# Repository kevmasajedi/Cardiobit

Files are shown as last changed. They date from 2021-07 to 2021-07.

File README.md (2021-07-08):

# CardioBit
## A Smart, Opensource and Affordable Electrocardiography Platform
CardioBit is an architecture for building IoT capable, precise, scalable and cost-efficient ECG Devices. IoT-capability and affordability are the central dogmas of this architecture. This is mainly achieved by using opensource hardware, minimum reliance on specialty components, offloading signal processing tasks to the server and avoiding the use of costly isolation components - yet ensuing safety by relying solely on battery power.

## Introduction
In the wake of COVID-19 pandemic, in many countries throughout the world, medical infrastructure is seriously overwhelmed by a novel coronavirus. The vast majority of medical equipment are heavily patented and are sold in small volumes. Further, there is evidence that some entities actively prevented medical treatments from being deployed, even in the current pandemic. This model obviously fails during critical times. On the other hand, deployment of opensource hardware and software platforms, can result in significant cost reduction as well as increased critical preparedness. (Pearce 2020)

The potential of opensource platforms to facilitate the formation of inclusive, potentially worldwide research communities, have also captured my imagination. Economically
viable solutions can be derived out of the core architecture discussed here, and can be manufactured and deployed throughout the world, in a distributed fashion. In additon, a 12-lead proof-of-concept hardware is provided.

## Background
Readers are assumed to have a minimal background in physiology and electrical engineering. Namely, they are assumed to be familiar with the basic morphological characteristics of electrocardiogram and their physiological significance, and familiarity with ohm’s law, impedance, basic circuit theory, RC analog filters and basic operational amplifier circuits. However, prospective readers are encouraged to continue, as proper reference for further consultation is given in due course. For introductory topics in cardiac physiology see (Guyton and Hall 2015), and for basic introduction to electrical engineering concepts regard (Scherz and Monk 2016) and (Mancini and Carter 2009)

The simplest model for relating the electrical activity of the heart to the body surface potentials, is the single dipole model. As an action potential propagates through the cell, in the interface of depolarizing and resting tissue, there’s an intracellular current flow in the same direction of the action potential propagation. There is also an equal extra cellular current flowing against the direction of propagation. Therefore, charge is conserved and all the current loops in the conductive media form a single field, called “dipole field” (Figure 1). (Gari, Francisco and Patrick 2006)

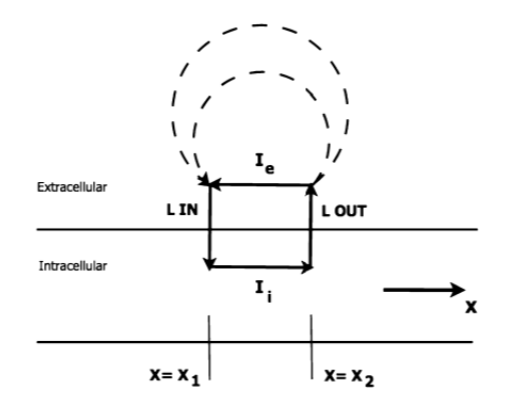
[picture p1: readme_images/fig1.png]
Figure 1. Flow of bioelectricity in current loops, presenting four segments: an outward traversal of the cell membrane, an extracellular segment, an inward traversal of the cell membrane and an intracellular segment.
 

For modeling purposes, all the individual current dipoles can be considered to originate at a single point in space, and the total electrical activity of the heart can be represented as a single dipole, whose magnitude and direction is the vector summation of all the individual dipoles. (Madeiro, et al. 2019)

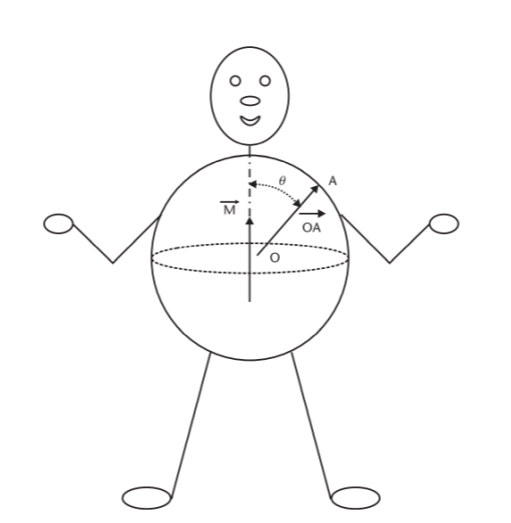
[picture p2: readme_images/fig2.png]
Figure 2. The Idealized spherical torso with the centrally located cardiac source


Let M(t) be the resultant vector which changes in the magnitude and direction as the function of time, potential distribution on the torso can be obtained by solving the Laplace’s equation as: (Gari, Francisco and Patrick 2006)

 

Where 𝜎 is the conductivity of the body electrolytic medium, |M(t)| is the magnitude of heart vector, θ(t) is the angle between the heart vector M(t) and the lead vector joining the center of the sphere to the point of surface potential measurement (Figure 2). Therefore, potential difference between two points in the torso can be given as: (Gari, Francisco and Patrick 2006)

 

Where 𝐿𝐴𝐵(𝑡) refers to the lead vector containing different points A and B of observation (e.g., electrodes) on the torso. For more elaborate discussion regarding the derivation of the abovementioned equations, please refer to (Mark 2004)

###  🎯 Design Decision I: Platform must be able to reconstruct 12 virtual leads from a reduced lead set
Equation 2.2 is important, as it states that the potential vector between two given electrodes (which essentially comprises the ECG signal in the respective lead) can be reconstructed if M(t) and the angle between M(t) and the lead vector 𝐿𝐴𝐵(𝑡) are known. As demonstrated later in the proof of concepts, the reconstruction of a virtual 12-Lead ECG from a reduced lead set is attempted in software, with satisfactory results.

However, it should be emphasized that equation 2.1 is derived with the implicit assumption of body as an idealized spherical torso, as shown in Figure 2. As a matter of fact, not only torso is far from an idealized sphere, but also it has non uniform conductance 𝜎 and its impedance can change during the cycle of respiration as well. (Gari, Francisco and Patrick 2006) So, for critical applications (e.g., in critically ill, unstable patients or in studying conditions that require exact monitoring) it is highly recommended to rely on standard 12-Lead ECG as opposed to the virtual case discussed above. 

In overall, this ability is helpful in that it provides the clinicians in unprivileged areas with more data without additional costs. Thus, it helps in cases which wide availability of ECG monitoring is the primary goal. For example, when secondary prevention (i.e., screening) of ischemic or heart rhythm disease is to be performed on a disperse population in a large geographic area.

***

## Signal Acquisition:
### Electrode-Patient Interface:
The electrical activity of the heart is propagated throughout the body by ions. To measure this activity at body surface, conversion of ions to electrons, is needed. This conversion happens at electrode-patient interface. When a metallic electrode (most commonly silver-silver chloride) is in contact with an electrolyte (skin or electrode gel), an electrochemical reaction occurs by ionexchange. Metal atoms (𝑀) tend to lose n electrons and pass into the electrolyte as metal ions (𝑀+𝑛 ) causing the electrode to become negatively charged with respect to the electrolyte: (Webster 2006)

 

Similarly, under equilibrium, ions in the electrolyte take the reverse direction of the equation (3.1). The electrode becomes positively charged with respect to the electrolyte as a result. (Webster 2006)

 

Under equilibrium condition, rate at which metal atoms lose electrons and pass into the electrolyte is exactly balanced by the rate of equation (3.2). Thus, the current flowing in one direction, cancels out the current flowing in the opposing direction, resulting in zero net current flow. However, a potential difference is found to exist between the electrode and electrolyte and depends on the position of the equilibrium between two processes (3.1) and (3.2). This potential is termed as half-cell potential, and can be calculated by the Nernst Equation (3.3) (Webster 2006)

𝐸0 is the standard half-cell potential measured relative to the standard hydrogen electrode, R is the universal gas constant, n is the number of electrons involved in the reaction, T is the absolute temperature in Kelvin. F is the faraday’s constant.

Since an ECG signal is obtained by two equal electrodes for each lead, it can be assumed that half-cell potentials are equal and offset voltage at the input of differential amplifier is zero. In practice, small differences in the properties of electrodes result in a dc offset voltage, which can sometimes change over time. (Madeiro, et al. 2019)

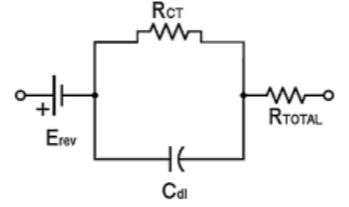
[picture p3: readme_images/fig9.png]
Figure 3. Electrode-Patient Interface Equivalent Circuit. 𝐶𝑑𝑙 the double-layer capacitance; 𝑅𝐶𝑇 the charge transfer resistance; 𝑅𝑇𝑂𝑇𝐴𝐿 lead and electrode resistances and 𝐸𝑅𝐸𝑉 the equilibrium (Nernst) potential.


Further, as positive ions are attracted by the electrode and negative ions by the electrolyte, a double layer capacitance is created at the electrode-patient interface. Also, due to the electrochemical reactions in the interface, some dc current can leak across the double layer. The amount of leak is proportional to charge transfer resistance which is calculated by the equation (3.4) where 𝑖0 is the current flowing across the interface in both directions (no flow under equilibrium, as discussed before). The equivalent circuit is shown in Figure 3. (Madeiro, et al. 2019) Note that equations (3.3) and (3.4) are only of theoretical interest here.

 

###  🎯 Design Decision II: Cost-optimized solutions should be supplied with higher voltage
DC offset voltage discussed above, can be as high as 300mV which is enormous when compared to typical 1.8mV amplitude of the ECG signal (Lee and Kruse 2008). The dc offset can be reduced by the use of high-quality electrodes or significantly suppressed with specialty circuits (Huang, Huang and Li 2018). However, in accordance with the design principles discussed in the abstract of this article, a simple rule of thumb is proposed instead: Use higher supply voltage, when designing cost-optimized solutions.

To put this design decision in better context, we need to slightly deviate from the flow of the discussion:

>As ECG signal is very weak with only 0.5µV – 4mV of amplitude and is susceptible to interference [e.g., 50 or 60Hz AC noise which is present in virtually all indoor environments], it needs to be amplified before processing and analysis. (Huang, Huang and Li 2018)

>A high dc offset voltage can quickly saturate a low-voltage circuit and limit the amount of achievable amplification. For example, a 3V supply voltage (equivalent to -1.5v to +1.5v dual supply), can be easily saturated by only a 5 times front-end amplification. Thus, only 2x to 3x first-stage gain can be reasonably applied. A high-resolution signal can still be obtained after a second-stage amplification and by the use of a high-precision analog-todigital converter (ADC). But as discussed later, due to low front-end amplification the noise profile will not be satisfactory. In addition, high-precision ADCs can be costly and usually have far slower sampling rates.

Thus, for designing cost-optimized solution, a supply voltage of at least 12V (-6.0v to +6.0v) is recommended. As CardioBit is designed for battery-powered operation, and high-capacity 3.7v 18650 Lithium-Ion cells are widely available with ever decreasing cost (Warner 2015), such supply voltage can be provided with 3 to 4 cells in series, allowing for a compact form-factor for the final, assembled device.

***

### Surface Lead Systems:
The standard 12-Lead ECG is a noninvasive representation of the electrical activity of the heart. This lead system rests on the theoretical foundation of classical lead theory introduced by Einthoven et al. (Madeiro, et al. 2019) This theory assumes a single time-varying dipole in 2- dimensional space to represent electrical activity of the heart, and assumes human body as a homogenous conductor. Later, Burger and van Millan improved and generalized the theory (Burger and van Milaan 1948) with regard to 3-dimentionality and non-homogenous conductance of the body. Yet, their theory still rests on the fixed-dipole hypothesis, thus allows for the derivation of the potentials at a given instance, anywhere on the body surface (Macfarlane, et al. 2011). As noted in [Design Decision I](https://github.com/kevmasajedi/Cardiobit/blob/main/README.md#-design-decision-i-platform-must-be-able-to-reconstruct-12-virtual-leads-from-a-reduced-lead-set), these assumptions are not completely solid.

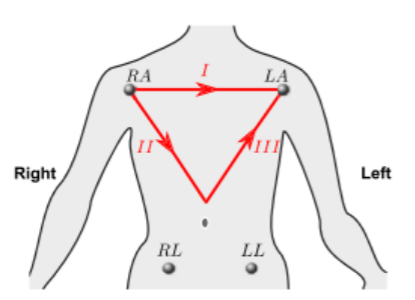
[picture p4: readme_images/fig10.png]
Figure 4. Bipolar Limb Leads.


12 Leads on this system are composed of 3 bipolar limb leads(I, II, III), 3 augmented unipolar limb leads (aVR, aVL and aVF) and 6 unipolar chest leads (𝑉1 𝑡𝑜 𝑉6). Bipolar limb leads are defined by equations 3.5, 3.6, 3.7. (Figure 4). Right leg electrode is used for reducing electromagnetic interference, and can be placed anywhere at body surface. It is placed at right leg for convenience. (Madeiro, et al. 2019).

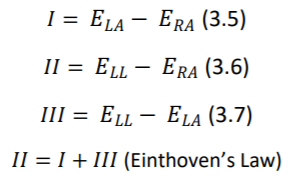
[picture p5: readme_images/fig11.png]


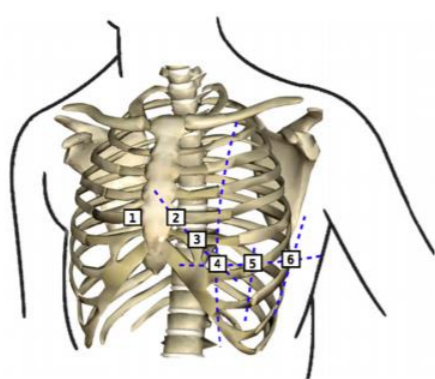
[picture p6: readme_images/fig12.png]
Figure 5. Position of unipolar chest leads


Potentials of unipolar chest electrodes (𝑉1 𝑡𝑜 𝑉6) is measured relative to Wilson Central Terminal (WCT), which is the normalized sum of the potentials of 𝐸𝐿𝐴, 𝐸𝑅𝐴 and 𝐸𝐿𝐿. (Equations 3.8 and 3.9) (Madeiro, et al. 2019)



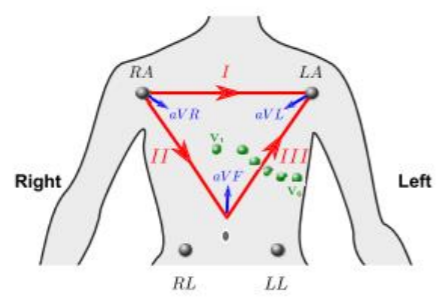
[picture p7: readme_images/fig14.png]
Figure 6. Standard 12-Lead System


Augmented unipolar limb leads, comprise the remaining three leads. The same set of electrodes from bipolar leads are used (𝐸𝐿𝐴, 𝐸𝑅𝐴 and 𝐸𝐿𝐿) as positive electrodes and negative electrode is a modified version of the Wilson Central Terminal called of GT. (equations 3.10 through 3.12) (Madeiro, et al. 2019)

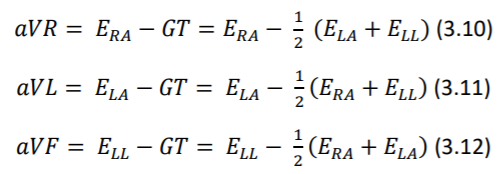
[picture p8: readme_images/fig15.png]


###  🎯 Design Decision III: Technical issues should be openly discussed, anyone’s contribution is to be welcomed
A variety of other lead systems are proposed, including Frank, reduced Frank, EASI or various three or two lead configurations. (Gari, Francisco and Patrick 2006). But the standard 12-Lead system has by far the widest adoption in clinical practice. Thus, other configurations are not discussed further. 

However, CardioBit is opensource in hardware and software and it can be adopted for any given lead set, by any interested researcher. In fact, as the author, I’ll be delighted If I see such actions taken by the potential research and development community. I believe community, can shed more light on the issue of practicality of virtual 12-Lead ECG reconstruction from a reduced lead set, provide a quantitative measure of accuracy for such reconstructions, or even come up with a more theoretically solid method of reconstruction (e.g., based on the modern concept of leadfield instead of lead-vector)

In that spirit, I like to echo a section of *ST Segment Monitoring Practice Guideline Working Group*’s recommendation regarding the use of reduced lead sets, which is further discussed by (Gari, Francisco and Patrick 2006):

- If only two leads are available for ST segment monitoring (for patients with acute coronary syndrome), lead III and V3 should be used.
- The best three-lead combination is III-V3-V5
- V1, is considered the best lead to monitor for cardiac arrhythmias
- The use of at least three chest leads (V3, V4, V5) is recommended for ST analysis

The provided proof-of-concept of the CardioBit platform’s core architecture, is designed for acquisition of 2 bipolar limb leads and 2 unipolar chest leads. User (whether clinician, researcher or developer) can decide which respective two leads he or she wants to use. As noted, reconstruction of virtual 12-lead ECG from the chosen leads is attempted in software. It is left up to user to decide whether to use this feature or not. For more information, please regard the factors noted in  [Design Decision I](https://github.com/kevmasajedi/Cardiobit/blob/main/README.md#-design-decision-i-platform-must-be-able-to-reconstruct-12-virtual-leads-from-a-reduced-lead-set)
***
## Electrical Design
### The Characteristics of Measured Biopotential

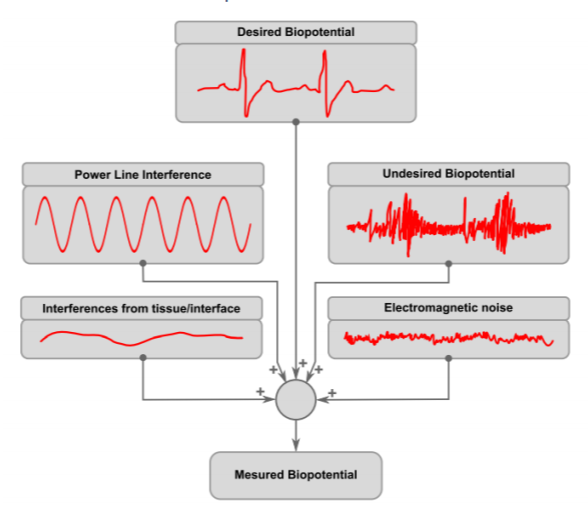
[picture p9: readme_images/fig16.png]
Figure 7. Components of measured biopotential. (Credit: Madeiro, et al. 2019)


As stated before, surface potentials representing ECG signal are very weak (a few millivolts maximum) and are riding on a comparatively enormous offset voltage (hundreds of millivolts). (Lee and Kruse 2008) To complicate matters further, these signals are often contaminated with biopotential activity of muscles and nerves beneath the electrodes, 50Hz/60Hz AC powerline interference, low frequency motion artifacts and all sorts of high frequency electromagnetic noise (Madeiro, et al. 2019)

Among these parasitic sources, the AC interference may be the most troublesome. Low frequency motion artifacts can be dealt with by good skin preparation and good electrode adhesion. Also, biopotential artifacts of nerve and muscle activity will be negligible if patient remain still and relaxed at a comfortable position. Lastly, high frequency noise, can be easily suppressed by a simple analog RC filter and later by digital filtering. Conversely, AC interference is present virtually anywhere and its frequency falls in the normal frequency range of ECG signal (0.05Hz – 250Hz)

Unfortunately, AC interference is unavoidably present in any clinical situation. This interference can be of two independent types: magnetic and electric: A changing magnetic field produced by AC powerlines can induce in any nearby conductive loop, an electromotive force, which results in an ac potential. A changing electric field can also produce interference by causing ac currents to flow to ground through the system. (Huhta and Webster 1973)

The magnetic interference is directly proportional to the area of the loop formed between two electrode leads and reducing this area is the best way to reduce this type of interference. Expensive shielding of the wires does not prevent this kind of interference. (As shown in Figure 8.) (Huhta and Webster 1973)

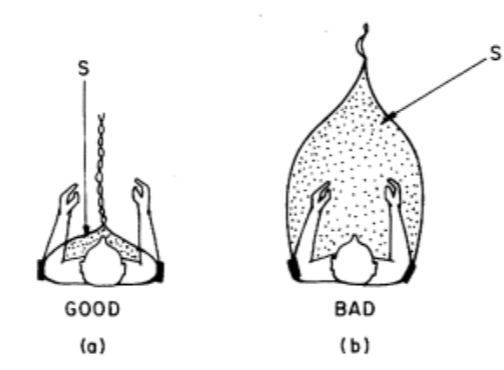
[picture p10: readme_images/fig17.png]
Figure 8. AC noise pickup by magnetic interference. (Credit: Huhta and Webster 1973)


The electrical interference is modeled as the capacitive coupling of AC powerlines to lead wirings, which results in displacement current induced in the respective leads, because the length of the leads is almost the same and the wires run closely together, this displacement current should be approximately equal in each lead. (Huhta and Webster 1973)

Assuming that electrodes have perfectly the same electrical impedance, such displacement current should be rejected. Because, the front-end differential amplifier, only amplifies the difference between the voltages of the two inputs. In other words, as impedance of both electrodes is the same, the displacement current, results in induction of exactly the same voltage in them. This can be easily stated using generalized ohm’s law (Equation 3.13).



Where 𝑉_𝐴𝐶 is the AC interference potential, 𝐼_𝐷 is the displacement current and Z is the impedance in respective inputs A and B. It is observed that 𝑉_𝐴𝐶 is induced by unbalance of the two impedances (the term 𝑍_𝐴 − 𝑍_𝐵 being non-zero). (Huhta and Webster 1973)

That being said, it should not come as a surprise, that no two electrodes are perfectly the same in real world. Electrode impedance at 60Hz may range from less than 1 KΩ up to 100 KΩ. Given typical values of 6 nA of 𝐼𝐷 in a 3-m length of unshielded wire, and typical impedance imbalance of 5KΩ, induced potential (𝑉𝐴𝐶) would be about 30µV which is roughly 3 percent of the ECG potential. (Huhta and Webster 1973)

Author should note here that in the experimentation with lower quality, cheaper disposable electrodes, far higher impedance imbalance has been observed and induced potential frequency observed to be as much as 10% of the QRS potential. Such observations influenced the [Design Decision IV](https://github.com/kevmasajedi/Cardiobit/blob/main/README.md#-design-decision-iv-use-heavy-dsp-instead-of-fancy-analog-circuits) which will be discussed in due course.

### Analog Front End Circuit
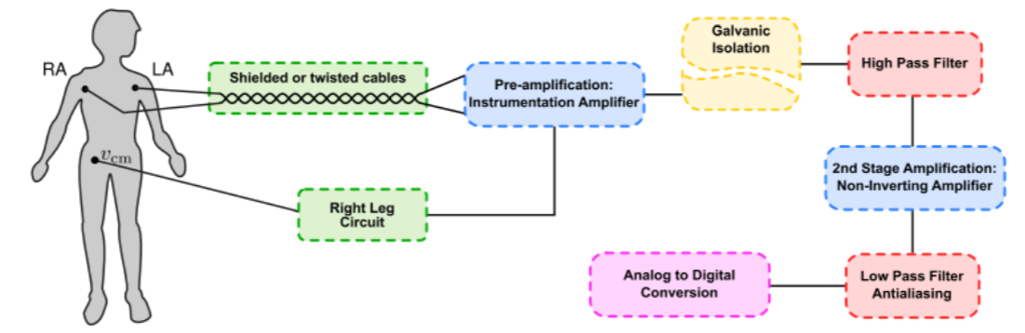
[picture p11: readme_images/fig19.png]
Figure 9. A classical topology of ECG analog front end topology. (Credit: Madeiro, et al. 2019)

Figure 9, shows a classical topology of ECG analog front end signal conditioner. Here, the intention of each stage in this block diagram is briefly discussed:

#### Shielded or Twisted Cables:
- Twisted cables minimize the area occupied by the loop forming between electrode leads and the body, thereby reduce the magnetic interference of AC powerlines. As discussed in the section 3.3.1 and shown in Figure 8. Shielding provides a measure against electrical interference of AC powerlines, by providing a grounded surface near the lead wires, thereby significantly reduces capacitive coupling of powerlines with lead wires. Consult (Huhta and Webster 1973) for more detailed discussion.

#### Pre-Amplification by Instrumentation Amplifier:

- Instrumentation Amplifiers are modified types of operational amplifiers. They are differential amplifiers with a very high (theoretically infinite) input impedance and improved CMRR. This large input impedance, is essential to ensure no current is being drawn from the body, and thus the small voltage of ECG signal is properly measured. In short, the chain of reasoning for this, is very similar to that of well-known ideal voltmeter, which should have infinite resistance and no current should flow through it. See (Horowitz and Hill 2015) or (Scherz and Monk 2016).
- Common-Mode Rejection Ratio (CMRR) indicates the ratio between the differential gain of an amplifier (𝐺𝐷) and its common-mode gain (𝐺𝐶). (Equation 3.14) Common mode signals are those that appear simultaneously on both inputs (e.g., that of 60/50-Hz powerline interference). Ideally, CMRR of a differential amplifier should be infinite. However, that’s not achievable in practice. Instrumentation amplifiers enjoy a higher CMRR than those of ordinary operational amplifiers, due to their special configuration. The value of CMRR changes with gain and frequency, and typically ranges between 80dB to 120dB. See (Horowitz and Hill 2015).
- Last to be noted under this topic, is the necessity of pre-amplification per se. As discussed before, the desired ECG signal is very weak and is floating on a large-by-comparison voltage offset, created by unequal Nernst potential in respective electrodes. This limits the amount of gain applicable to the first stage amplification. In addition, low frequency noise resulting from poor skin preparation or poor electrode adhesion can further complicate the problem. Thus, a large first-stage gain would result in quick saturation and/or large wandering of output signal of the circuit. Dividing amplification in two stages, can significantly alleviate these problems and yet adequately amplify the signal to meet the dynamic range of analog-to-digital converter. (Madeiro, et al. 2019)
- Author proposes a coarse rule of thumb for determining first-stage gain: divide supply voltage by 0.3 and do not exceed one-fourth of the result. For example, a supply voltage of 12v (+6v to -6v) should have maximum first stage gain of ( 12/0.3 × 1/4 = 10). The divisor 0.3 comes from taking into account a typically high electrode offset voltage of ∓ 300mV. It is divided by four to ensure amplified offset does not saturate more than half of negative or positive voltage rails.

#### Right Leg Drive Circuit:
- This circuit inverts and amplifies the common-mode voltage and feeds it back to the body. As a result, it can help to reduce noises that are induced on both of the electrode leads (e.g., AC powerline noise). (Madeiro, et al. 2019) Unfortunately, this circuit can easily become unstable, and thus not implemented in CardioBit proof-of- concept hardware (more on the reason in [Design Decision IV](https://github.com/kevmasajedi/Cardiobit/blob/main/README.md#-design-decision-iv-use-heavy-dsp-instead-of-fancy-analog-circuits)). This circuit is extensively discussed in literature and interested readers are referred to (Webster 2006)

#### Galvanic Isolation:
- Safety precautions should be taken seriously when a circuit that is connected to the mains electricity, comes into contact with human subject. Even very small current leakages (less than 100µA) can induce lethal ventricular fibrillation in catheterized human subjects. 
- In such circumstances, circuit board must be segmented into isolated and non-isolated sections. These sections must be separated by at least 10mm of free space from each other (depending on the dielectric constant of the PCB) Isolated sections should receive power from non-isolated section via DC-to-DC converters. Similarly, information (ECG signal) is transmitted back to the non-isolated parts through opto-isolators or isolation amplifiers. (Gari, Francisco and Patrick 2006)
- ⚠ As discussed in the [Design Decision V](https://github.com/kevmasajedi/Cardiobit/blob/main/README.md#-design-decision-v-design-for-battery-powered-operation-only), and in accordance with the design principles discussed in the abstract, **CardioBit, is designed ONLY for low-voltage DC battery-powered usage.** The proof-of-concept circuit is not isolated and should not be directly (via AC-to-DC adapter) or indirectly (via USB port to a mains-powered PC or even a laptop that is connected via an adapter to AC power) connected to the wall outlets, unless it is completely disconnected from human subject. The operator, is responsible for any shortcomings in protecting patient safety, when he or she ignores these precautions.
- As CardioBit is opensource, any community developed hardware is advised to come with precise documentation clearly describing the specific solution’s do’s and don’ts regarding patient safety.

#### High-Pass Filter:
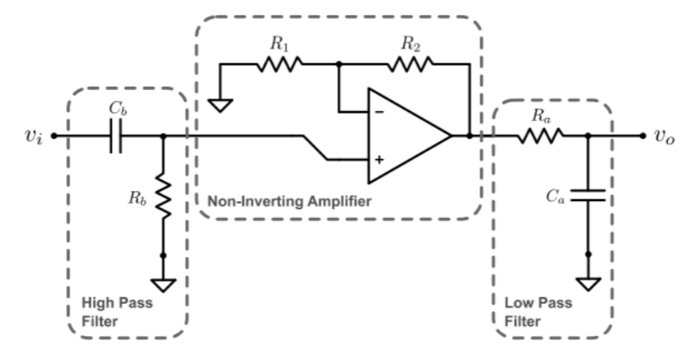
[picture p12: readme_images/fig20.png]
Figure 10. Depicting HPF, Second-Stage Amplification and LPF stages


- As previously discussed, half-cell potential differences at electrodes result in a DC offset which gets amplified in the first stage and can possibly saturate the voltage rails if high amplification is applied. In addition, changes in skin moisture, temperature, muscle tremor, movement, electrode gel leakage and patient’s breathing, result in slowly varying electrode impedance which manifests itself as a slow wandering of the ECG baseline. (Madeiro, et al. 2019) A simple RC filter can ground the signals below a cutoff frequency 𝑓𝑐 , which is determined by choosing the values of the resistor R and the capacitor C. (Equation 3.14) However as discussed in (G), using an active filter might be a better option.



#### Second Stage Amplification:
- As high-pass filter, removes the effect of offset voltage, higher amplification can be achieved in the second stage. The amount of the amplification should be determined by both considering supply voltage of the circuit and dynamic range of the analog-to-digital converter. One must ensure a high-voltage QRS complex would not saturate the voltage rails. Minimum amplification for a desirable dynamic range can be determined by looking for the u-waves in the acquired signal. If these waves are readily recorded, it can be reasonably assumed that amplification is sufficient for analog-digital converter to faithfully record the signal.

#### Second Stage Amplification:
- As high-pass filter, removes the effect of offset voltage, higher amplification can be achieved in the second stage. The amount of the amplification should be determined by both considering supply voltage of the circuit and dynamic range of the analog-to-digital converter. One must ensure a high-voltage QRS complex would not saturate the voltage rails. Minimum amplification for a desirable dynamic range can be determined by looking for the u-waves in the acquired signal. If these waves are readily recorded, it can be reasonably assumed that amplification is sufficient for analog-digital converter to faithfully record the signal.

#### Low Pass Filter:
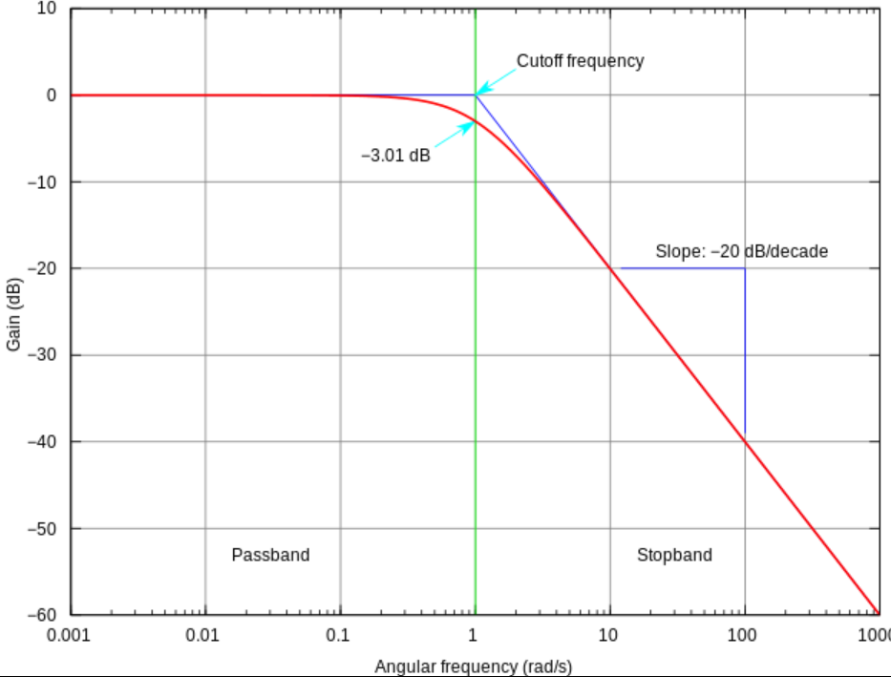
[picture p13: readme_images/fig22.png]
Figure 11. Frequency response of RC filters. Roll-off of simple RC low pass filters, is only about -20 dB/decade (credit: wikipedia)


- high frequency electromagnetic interference, and skeletal muscle activity, can also contaminate the recorded biopotential, especially during exercise or under 24/7 continuous (Holter) monitoring. These high frequency components should be filtered, in a way that does not cause distortion on ECG signal (e.g., blunting of the QRS peak). Attempting to rely solely on the slow sampling frequency of analog-to-digital converter (ADC), to filter such components, will result in a signal corrupted by aliasing effect. Refer to (Parker 2017) for an introduction.
- In order to avoid aliasing, Nyquist theorem dictates the cutoff frequency of the low pass filter (equation 3.14) should be less than half the sampling frequency of ADC. Kligfield, et al. suggested 0.05 Hz to 250 Hz to be the frequency band of desired ECG signal. If adult patients are under monitoring, the cutoff of the lowpass filter can be reduced to 150 Hz. So, the ADC must feature a sampling frequency of at least 301 Hz.
- A simple low-pass filter is used in the proof-of-concept of the core architecture. But theoretically, this may not be a good choice. First, simple RC filters suffer from a poor rolloff of about -20 dB/decade. Meaning signals with 10 times the frequency of filter’s cutoff will still be present with one-tenth of original voltage. So, noises which have frequencies close to the cut-off, will remain significant and may still cause prominent aliasing to occur.
- High-order active filters can instead be used with more ideal performance, but designer needs to beware occasional ringing behavior near cut-off frequency. High-order Bessel filters are recommended for their linear response and minimal distortion (Madeiro, et al. 2019). I avoid discussing details here, as they are far from the scope of this article. However, in [Design Decision IV](https://github.com/kevmasajedi/Cardiobit/blob/main/README.md#-design-decision-iv-use-heavy-dsp-instead-of-fancy-analog-circuits), I discuss why simple RC filters are used in core architecture’s proof-of-concept.

#### Analog to Digital Conversion:
- Lastly, the acquired biopotential will be converted to digital representation by a delta-sigma analog-to-digital converter, with a sampling frequency of at least twice the cut-off frequency of the low-pass filter. The digital signal will be further processed with embedded microcontroller (Based on Arduino or ESP8266 platforms) as discussed later.

### 🎯 Design Decision IV: Use Heavy DSP Instead of Fancy Analog Circuits
This design decision, has been referred to, as early as Section 3.3.1, in relation to the issue of impedance imbalance of low-quality electrodes, and later, in 3.3.2 (C), in relation to right-leg circuit, and then, in 3.3.2 (G) in relation to RC filters. However, actual presentation of this designdecision has been delayed until now, because sufficient background should have been discussed for it in order to make sense. 

The design decision IV is about the approach to noise-suppression. As we learned, ECG signal is inevitably contaminated by noise. The issue is how to filter out and suppress the noise, without distorting the signal. Additionally, the core-architecture should be open-source, inclusive and cost-optimized. So, the solution, should not be overly elaborate, as it discourages contribution. Less-privileged users should also be kept in mind, so worst-case scenarios of poor-quality electrodes with large offset voltage and high impedance imbalance should be assumed throughout the design.

As a result, author decided against the use of right-leg drive circuit, as it is unstable by design and requires fine-tuning or fancy design techniques to work properly, which reduces scalability and inclusivity of platform. 

In the same spirit, simple first-order RC filters have been preferred over more complicated eighth-order active Bessel filters. However, in this case, the compromise sometimes manifests itself. Unfortunately, designer is sometimes forced to reduce cut-off frequency of the low pass filter below 150 Hz, to prevent aliasing in cases where sampling frequency of ADC is close to 300- Hz (which is not a rare issue in low-cost ADCs). Also, the R wave in the QRS complex may become mildly blunt, which may be tolerable in some applications, but not in some others. 

Such analog minimalism, will be later met with aggressive digital signal processing, on the server side, which can be flexibly tuned by the user through a web-based user interface. For example, User may enable, disable or set filtering frequency, etc. Please refer to (Parker 2017) for theoretical introduction on the subject. For enquiry about the detailed implementation of these features, please refer to the proof-of-concept hardware documentations. 

In overall, this decision may render the bare-bone, core-architecture unsuitable for some critical research or clinical applications. But then again, that’s not the intended use-case. The core architecture is designed as a starting platform for other solutions to be built upon it. I believe, overtime, a vibrant community can more than compensate such technical shortcomings. So, one must design the core platform as generic as possible, rather than prohibitively opinionated and elaborate. Later, more complete products can be made based on the core platform.

### 🎯 Design Decision V: Design for Battery-Powered Operation Only
CardioBit is also designed with a look toward distributed manufacturing. The casing, provided for the proof-of-concept hardware, can be readily made with a 3D printer, the PCB can be prototyped for just a few dollars and can be assembled in any electronicslaboratory with minimal equipment. Anyone, anywhere in the world can tweak the proof-of-concept hardware, or improve the design to make it more suitable for specific applications. 

With this great customizability, comes great concernsfor patient safety. As previously stated, less than 100µA of 60-Hz AC leakage current, can result in lethal consequences in catheterized patients. Although measures can be taken to ensure such leaks will not happen (e.g., by electrical isolation of the analog front-end and the use of isolation amplifiers), and healthy, nonhospitalized individuals, may have higher thresholds and less vulnerability, one cannot simply hope that all the design guidelines will be properly implemented in community-designed solutions. In this regard, the risk is simply too great even for minor mistakes. 

Thus, it was decided against the use of AC power, altogether. The core architecture along with its proof-of-concepts are designed ONLY for battery-powered operation. They should not be connected to mains powerlines, either via the charging adapter, or via USB port to an AC powered PC or even a charging laptop. Developers who want to use the USB port to test their prototypes, are advised to use an isolated USB hub to minimize dangers. 

I believe this design decision, not only results in far better patient safety, it also honors the design principles, as the total cost of both components and development will be driven significantly lower. This way, the platform will be far more forgiving in case of design/assembly errors and so it will remain inviting to young, less experienced minds. 

Additionally, in the long run, lithium batteries will become even more affordable, developed products will become more energy-efficient, and more portable, and can be used in remote locations and unprivileged off-grid areas.

## Digital Circuitry:
CardioBit platform, does not use custom digital circuits, and it is designed to be compatible with open-source electronics platforms like Arduino. Arduino is an open-source, easy to use hardware and software platform. The Arduino-based boards are readily available virtually everywhere in the world in multiple form-factors with affordable prices. 

Originally, Arduino is based on 8-bit AVR microcontrollers. But as hardware is opensource, versions based on ESP8266 32-bit processor are also developed based on Arduino platform. This chip is more powerful, and features more memory, along with full TCP/IP stack for Wi-Fi connectivity. Many open-source libraries are developed for this chip to be programmed with Arduino software, using Arduino integrated development environment (IDE) and Arduino programming language.

CardioBit is not opinionated about which platform, or microcontroller is used for further processing. One can use Arduino, Raspberry Pi, Orange Pi, CircuitPython or essentially any open or closed-source platform to pair with the analog front-end. Only requirements are to power the ADCs used in the circuit with native voltage of the platform (3.3v or 5v), choose the value of endstage resistors to divide the voltage to the suitable value, and connect to ADCs with a communication interface (e.g., SPI or I2C). Connectivity to internet should also be provided, either natively or by using Wi-Fi or Ethernet shields, as digital signal processing is offloaded to server-side.

However, to be on par with our design principles, we based the proof-of-concept models for the core-architecture on ESP8266 powered hardware and Arduino platform software. Low-cost, lowpower, readily available ADS1015 ADC chips are used and accessed via I2C. These can be directly swapped with ADS1115 chips for low lead-count solutions, as this has higher accuracy but lower sampling rate which renders it too slow for 12-Lead devices.

## ⚠ Safety and Precautions
As already stated, multiple times, CardioBit core architecture and its proof-of-concept implementations are designed **ONLY** for battery-powered operation. Operator is solely responsible for patient safety if he or she uses the device while it’s plugged into AC power adapter or non-isolated computer USB port. (Please refer to [Design Decision V](https://github.com/kevmasajedi/Cardiobit/blob/main/README.md#-design-decision-v-design-for-battery-powered-operation-only))

Also, the core architecture and its proof-of-concept implementations, are not equipped with voltage-limiting input circuitry, and should not be relied upon in mission-critical applications, especially when defibrillators or other electrosurgical equipment are to be used. In such cases, high-voltage induced between two leads by such equipment, can damage the internal circuits and render the device non-working.

## References
- Burger, H.C., and J.B. van Milaan. 1948. "Heart-vector and leads, Part I." British Heart Journal
- Einthoven, W, G Fahr, and A DE Waart. 1950. "On the direction and manifest size of the variations of potential in the human heart and on the influence of the position of the heart on the form of the electrocardiogram." American Heart Journal
- Gari, D.C., A. Francisco, and E Patrick. 2006. Advanced Methods and Tools for ECG Data Analysis. Artech House, Inc.
- Guyton, Arthur C., and John E. Hall. 2015. Guyton and Hall Textbook of Medical Physiology. Saunders.
- Horowitz, Paul, and Winfield Hill. 2015. The Art of Electronics 3rd Edition. Cambridge University Press.
- Huang, Ji-Wei, Tai-Ming Huang, and Fan-Yang Li. 2018. "Design of a low electrode offset and high CMRR instrumentation." IEEE.
- Huhta, James C, and John G Webster. 1973. "60-Hz Interference in Electrocardiography." IEEE Transactions on biomedical engineering.
- Kligfield, P., L.S. Gettes, J.J. Bailey, R. Childers, B.J. Deal, E.W. Hancock, G. van Herpen, and Kors. 2007. "Recommendations for the Standardization and Interpretation of the Electrocardiogram." Circulation.
- Lee, Stephen, and John Kruse. 2008. "Biopotential Electrode Sensors in ECG/EEG/EMG Systems." Analog Devices.
- Macfarlane, Peter W., Adrian Van Ooosterom, Olle Pahlm, Paul Kligfield, and Michiel Janse. 2011. Comprehensive Electrocardiology, Second Edition. Springer.
- Madeiro, Joao Paulo do Vale, Paulo Cortez, José Maria Da Silva Monteiro Filho, and Angelo Roncalli Alencar Brayner. 2019. Developments and Applications for ECG Signal Processing. Academic Press.
- Mancini, Ron, and Bruce Carter. 2009. Op Amps for Everyone. Newnes.
- Mark, Roger. 2004. Quantitative Physiology: Organ Transport Systems, Lecture notes from HST/MIT Open Courseware .
- Parker, Michael. 2017. Digital Signal Processing 101. Newnes.
- Pearce, Joshua M. 2020. "A review of open source ventilators for COVID-19 and future pandemics [version 2; peer review: 3 approved]." F1000Research 3,4
- Scherz, Paul, and Simon Monk. 2016. Practical Electronics for Inventors. McGraw-Hill Education.
- Warner, John. 2015. The Handbook of Lithium-Ion Battery Pack Design. Elsevier Science.
- Webster, John G. 2006. Encyclopedia of Medical Devices and Instrumentation. Vol I. Wiley-Interscience.

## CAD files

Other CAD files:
Proof of Concept/CardioBit 12-Lead PoC Routed PCB.DWG

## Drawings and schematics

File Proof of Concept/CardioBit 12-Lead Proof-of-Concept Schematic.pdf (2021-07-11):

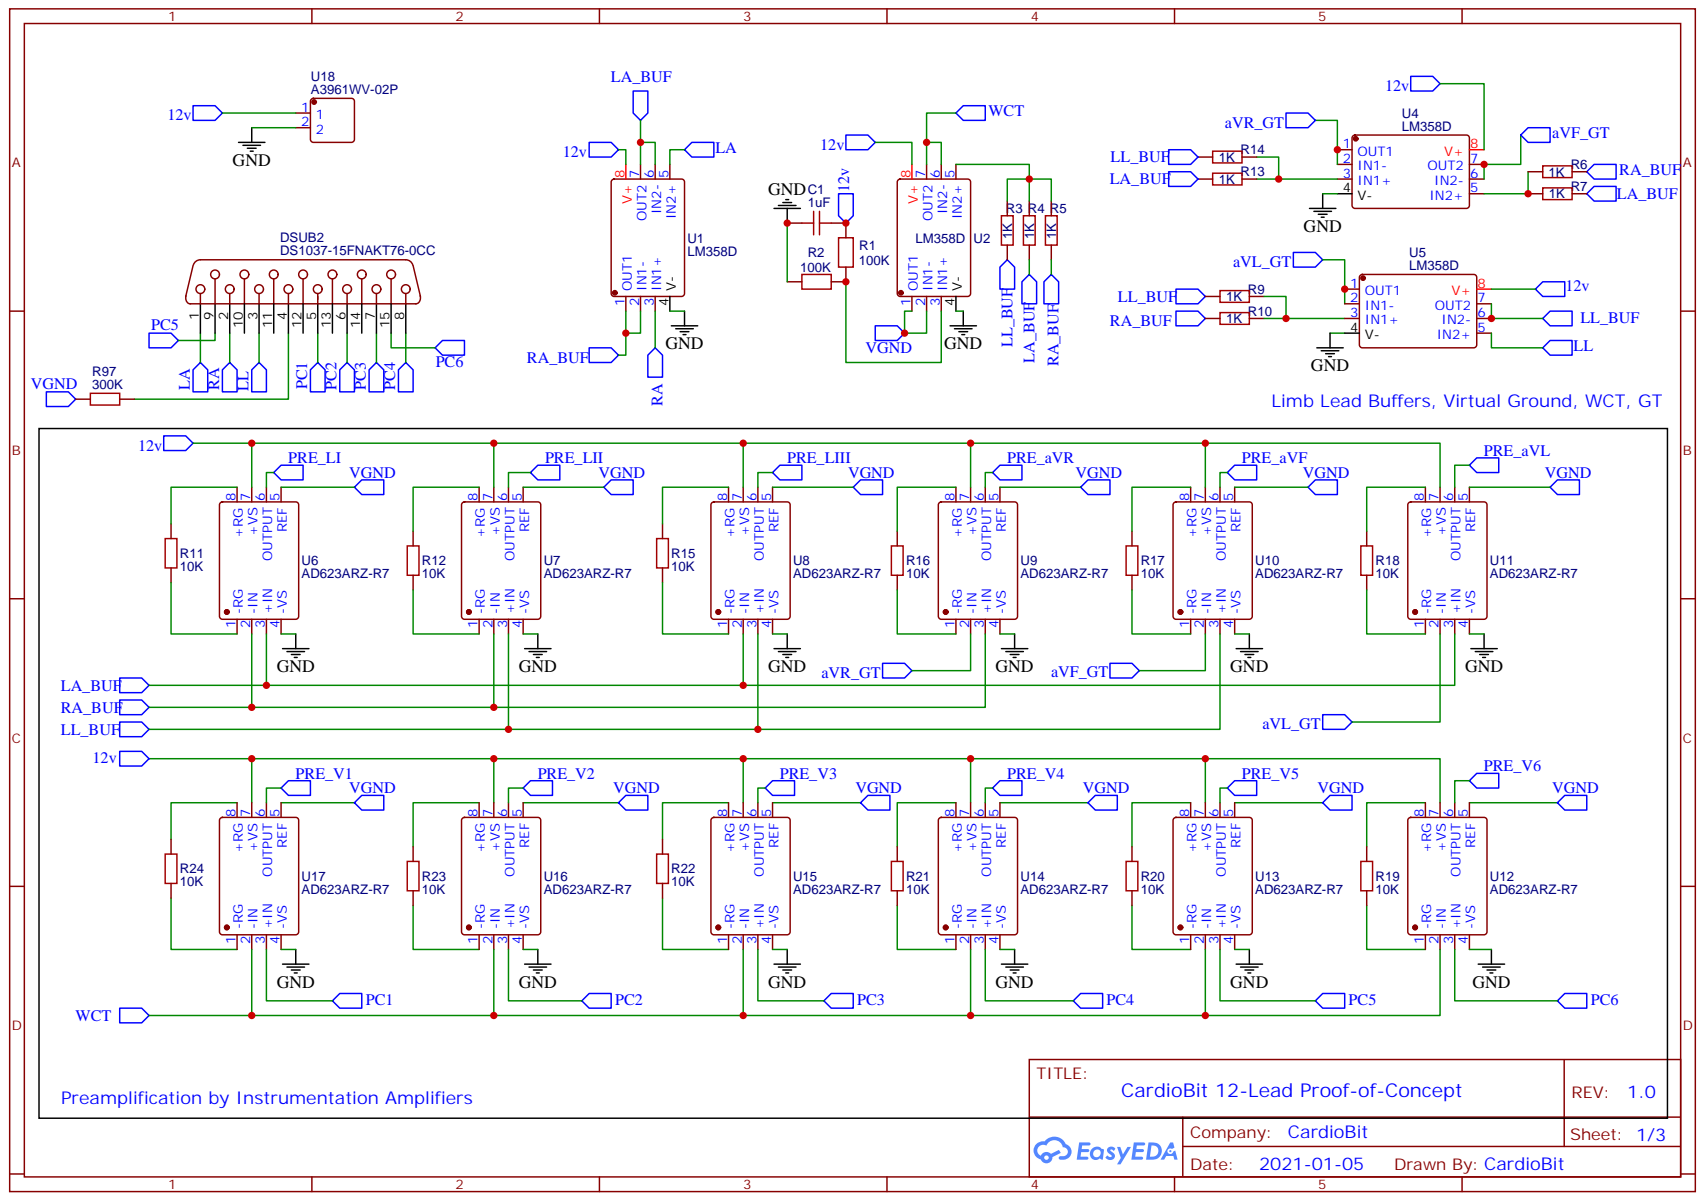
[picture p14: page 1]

GND
Limb Lead Buffers, Virtual Ground, WCT, GT

Preamplification by Instrumentation Amplifiers

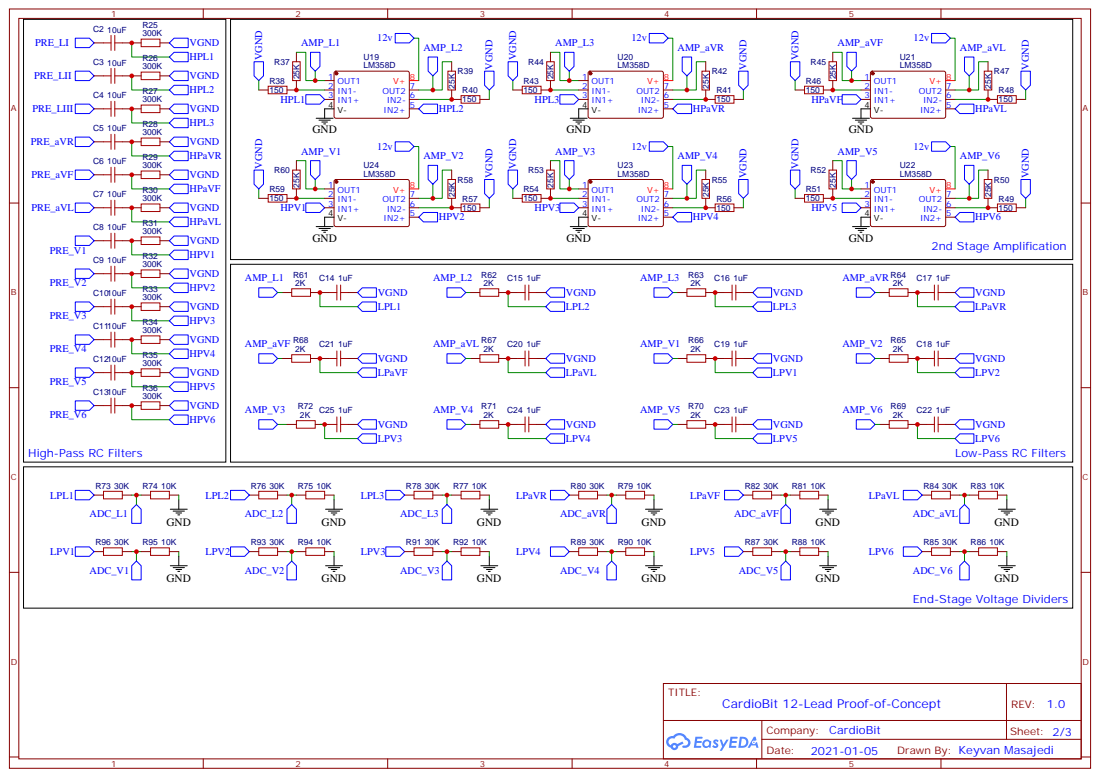
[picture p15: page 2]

High-Pass RC Filters

End-Stage Voltage Dividers

Drawn By: Keyvan Masajedi

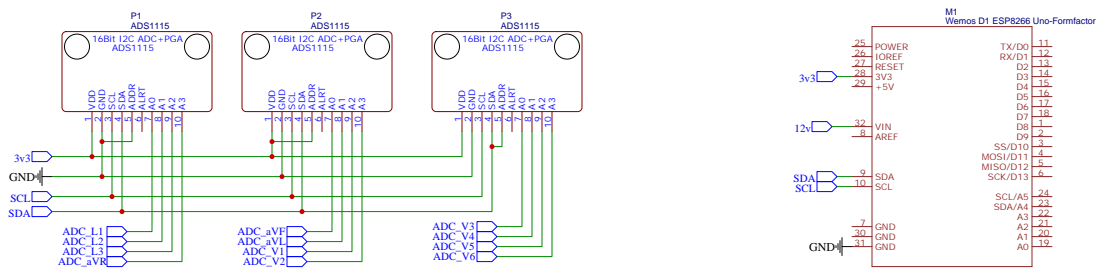
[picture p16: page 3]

Drawn By: Keyvan Masajedi
